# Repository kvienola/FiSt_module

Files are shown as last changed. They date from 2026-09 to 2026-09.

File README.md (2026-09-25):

# Fixation-Stimulus (FiSt) module for mirror-based adaptive optics scanning systems

This repository contains all the files related to the FiSt module to recreate it for your own use. The main goal of the module is to work as a stand-alone unit to be incorporated to existing imaging systems and allow precise stimulus delivery for optoretinographic measurements. The folders contain STL files that can be directly 3D printed, STP files that allow you to modify components according to your needs and Zemax files to simulate the fixation and stimulus path separately when altering components.

If you find the module and its files useful in your research, we kindly ask you to cite our publication XXX. 

__Maciej M. Bartuzel, PhD__ \
maciej.bartuzel@pwr.edu.pl

Department of Biomedical Engineering  
Wroclaw University of Science and Technology

## 1. 3D-printing
There are no restrictions what type of printing method you use or what type of filament. The Gen 1 module was printed using black PLA filament. We also recommend using high enough infill to ensure the rigidity of the different parts. And if you are not familiar with using thread inserts, we recommend printing a test block and practice. It is not difficult, but better to ruin a small sample block than ready-make larger component.

## 2. CAD design
Besides just the STL files, the folders contain also STP files that are meant for the community to develop further. If you make new version of certain components or add something useful, feel free to send us the files and we are more than happy to then include them in this repository.

## 3. Zemax simulations
The current two files (.zmx) simulate the fixation path and stimulus path separately using the currently selected components.

## 4. Future improvements planned for the module

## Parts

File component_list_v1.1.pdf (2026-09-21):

Component | Manufacturer | Model number | Quantity | Price per unit | Total cost | Description | Link
Aspherized Achromatic Lens | Edmund Optics | #49-656 | 1 | $113.95 | $113.95 | 9mm Diameter x 12mm EFL Aspherized Achromatic Lens | https://www.edmundoptics.com/p/9mm-diameter-x-12mm-efl-aspherized-achromatic-lens/10162/
Filter Holder | Edmund Optics | #54-996 | 1 | $67.50 | $67.50 | 15mm Sq., Fixed Filter Holder | https://www.edmundoptics.com/p/15mm-sq-fixed-filter-holder/11731/
75 x 75 mm Flat mirror | Edmund Optics | #88-541 | 2 | $301.00 | $602.00 | 75 x 75mm Protected Silver, λ/4 Mirror | https://www.edmundoptics.com/p/75-x-75mm-protected-silver-lambda4-mirror/30799/
Ø1" Achromatic Doublet | Thorlabs | AC254-075-A | 1 | $95.34 | $95.34 | f = 75 mm, Ø1" Achromatic Doublet, ARC: 400 - 700 nm | https://www.thorlabs.com/item/AC254-075-A
Ø2" Achromatic Doublet | Thorlabs | AC508-150-A | 2 | $132.19 | $264.38 | f = 150 mm, Ø2" Achromatic Doublet, ARC: 400 - 700 nm | https://www.thorlabs.com/item/AC508-150-A
Mounting Fork | Thorlabs | BP207 | 1 | $55.62 | $55.62 | Mounting Fork for Ø2" Pellicle Beamsplitters | https://www.thorlabs.com/item/BP207
Ø2" Pellicle Beamsplitter | Thorlabs | BP208 | 1 | $152.54 | $152.54 | Ø2" Pellicle Beamsplitter, Uncoated for 8:92 (R:T) Split Ratio for 400-2400 nm | https://www.thorlabs.com/item/BP208
XY adjustment plate | Thorlabs | CP1XY | 1 | $474.12 | $474.12 | 30 mm Cage XY Flexure Adjustment Plate | https://www.thorlabs.com/item/CP1XY
Iris Diaphragm | Thorlabs | CP20D | 1 | $111.60 | $111.60 | 30 mm Cage System Iris Diaphragm (Ø0.8 - Ø20 mm) | https://www.thorlabs.com/item/CP20D
Cage rod | Thorlabs | ER3 | 4 | $7.64 | $30.56 | Cage Assembly Rod, 3" Long, Ø6 mm | https://www.thorlabs.com/item/ER3
Kinematic mirror mount | Thorlabs | KMSS/M | 3 | $43.61 | $130.83 | Compact Kinematic Mirror Mount, Hex Adjuster, M4 Taps for Post Mounting | https://www.thorlabs.com/item/KMSS_M
Ø1" Bi-Convex Lens | Thorlabs | LB1294-A | 1 | $40.36 | $40.36 | N-BK7 Bi-Convex Lens, Ø1", f = 175.0 mm, ARC: 350 - 700 nm | https://www.thorlabs.com/item/LB1294-A
Fiber Patch Cable | Thorlabs | M45L01 | 1 | $95.21 | $95.21 | Ø400 µm, 0.50 NA, SMA-SMA Fiber Patch Cable, Low OH, 1 m Long | https://www.thorlabs.com/item/M45L01
2" x 2" Mirror | Thorlabs | PFSQ20-03-P01 | 1 | $144.90 | $144.90 | 2" x 2" Protected Silver Mirror | https://www.thorlabs.com/item/PFSQ20-03-P01
Retaining Ring | Thorlabs | SM1RR | 1 | $5.21 | $5.21 | SM1 Retaining Ring for Ø1" Lens Tubes and Mounts | https://www.thorlabs.com/item/SM1RR
Z-axis translation mount | Thorlabs | SM1ZB/M | 1 | $235.61 | $235.61 | Z-Axis Translation Mount, 30 mm Cage Compatible, M4 x 0.7 Tap | https://www.thorlabs.com/item/SM1ZB_M
Fiber adapter plate | Thorlabs | SM05SMA | 1 | $35.59 | $35.59 | SMA Fiber Adapter Plate with External SM05 (0.535"-40) Threads | https://www.thorlabs.com/item/SM05SMA
Fiber-coubled LED | Thorlabs | MINTF4 | 1 | $623.08 | $623.08 | 554 nm, 21 mW (Min) Fiber-Coupled LED, 1225 mA, SMA | https://www.thorlabs.com/item/MINTF4
LED Driver | Thorlabs | LEDD1B | 1 | $380.04 | $380.04 | T-Cube LED Driver, 1200 mA Max Drive Current (Power Supply Not Included) | https://www.thorlabs.com/item/LEDD1B
Power Supply for LED Driver | Thorlabs | KPS201 | 1 | $43.15 | $43.15 | 15 V, 2.66 A Power Supply Unit with 3.5 mm Jack Connector for One K- or T-Cube | https://www.thorlabs.com/item/KPS201
Threaded insert kit for 3D prints | FFVRVSS | 600Pcs M2-M6 Kit+Tools | 1 | $14.99 | $14.99 | 600+7Pcs Brass Threaded Inserts M2 M2.5 M3 M4 M5 M6 for 3D Printing | https://www.amazon.com/FFVRVSS-M2-M3-Threaded-Inserts/dp/B0FWCHPY4F/ref=sr_1_3
6mm Bore Dia Linear Motion Bushings | Various | not specific | 1 | $9.99 | $9.99 | Linear Bearings, 6mm Bore Dia Linear Motion Bushing with Double Side Rubber Seal | https://www.amazon.com/MELIFE-Bearings-Bushing-Machine-Printer/dp/B0CL3WD28D/ref=sr_1_4
M8 threaded rod, L = 200 mm | Various | not specific | 1 | $7.19 | $7.19 | 304 Stainless Steel M8-1.25 Fully All Threaded Rod, 250 mm length | https://www.amazon.com/Feelers-Stainless-M8-1-25-Threaded-Length%E3%80%90Pack/dp/B08FQL7LXV
6 mm unthreaded rod, L = 200 mm | Various | not specific | 2 | $6.17 | $12.34 | 304 Stainless Steel 6 x 200mm Round Rods | https://www.amazon.com/Eowpower-Stainless-Steel-200mm-Turning/dp/B072JPQX4Q
PLA filament | SUNLU | | 1 | $13.99 | $13.99 | PLA 3D Printer Filament, Black, 1KG | https://www.amazon.com/Printer-Filament-SUNLU-Dimensional-Accuracy/dp/B07XG3RM58
LCD screen + Driver board | Sharp | LS029B3SX01 | 1 | $94.81 | $94.81 | 2.9 Inch LCD Display LS029B3SX01 + driver | https://www.aliexpress.com/item/1005005565755501.html
Large dichroic mirror | CHROMA | T715LP | 1 | - | - | Dichroic BS with 715 nm cut-off, currently not in production. Alternative option: | https://www.idex-hs.com/store/product-detail/ff700_di01_25x36
A ball bearing | Various | not specific | 1 | $6.79 | $6.79 | A ball bearing with 8 mm ID and 12 mm OD. Maximum thickness of 12.7 mm. | https://www.amazon.com/MR128-2RS-Groove-Bearings-Robotics-Electric/dp/B0DXV273BX/ref=sr_1_1
| | | | | $3,854.90
| | | | | $2,808.63

Threaded inserts, rods, bearings do not need to be any specific manufacturer, as long as they are within specifications listed. Links are given as examples.

### Total cost

Excl. LED and driver

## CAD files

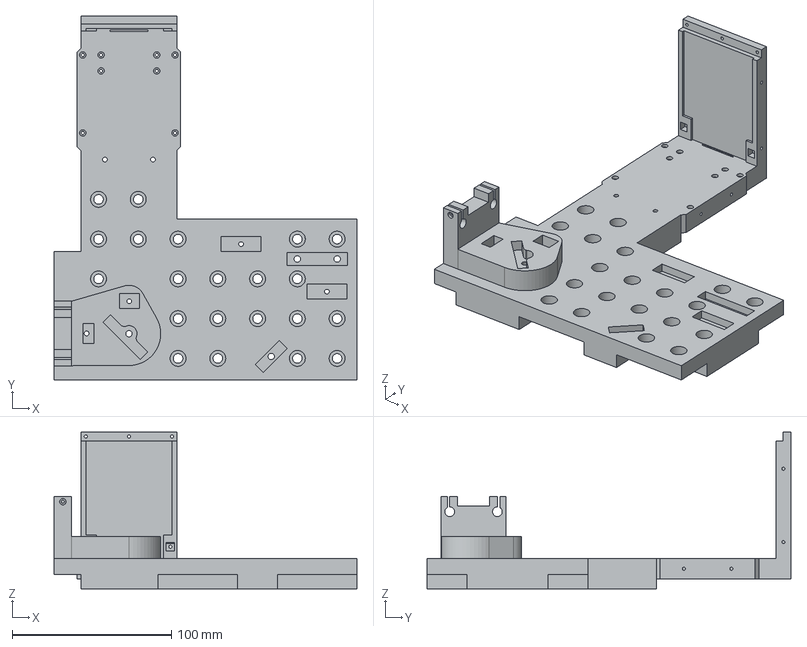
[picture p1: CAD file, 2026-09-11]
Main board/stp/01_mainboard.stp
190.5 x 228.8 x 98.7 mm

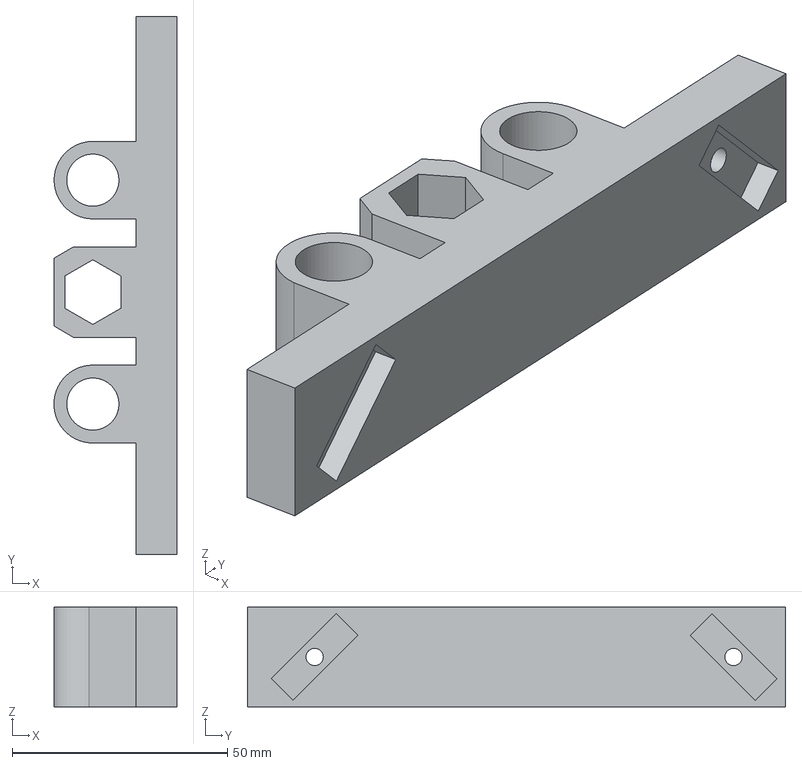
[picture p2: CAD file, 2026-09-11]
Badal stage/stp/13_badal_stage_top.stp
28.5 x 124.9 x 23.1 mm

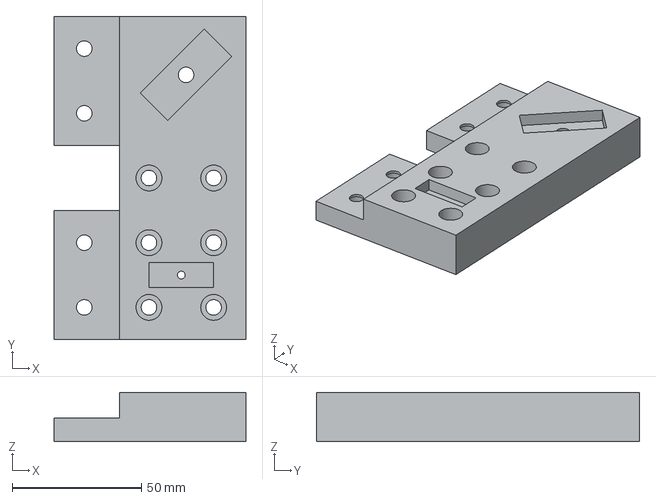
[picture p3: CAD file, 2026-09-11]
Imaging board/stp/23_dichroic_board.stp
74.2 x 125.0 x 19.1 mm

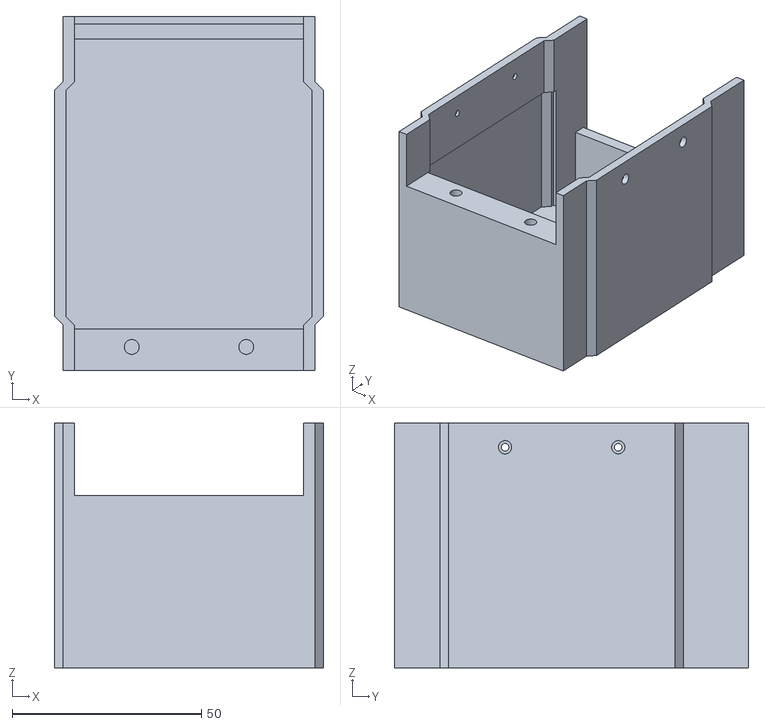
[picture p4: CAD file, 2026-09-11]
Main board/stl/04_pcb_boards_housing.stl
71.0 x 93.5 x 64.6

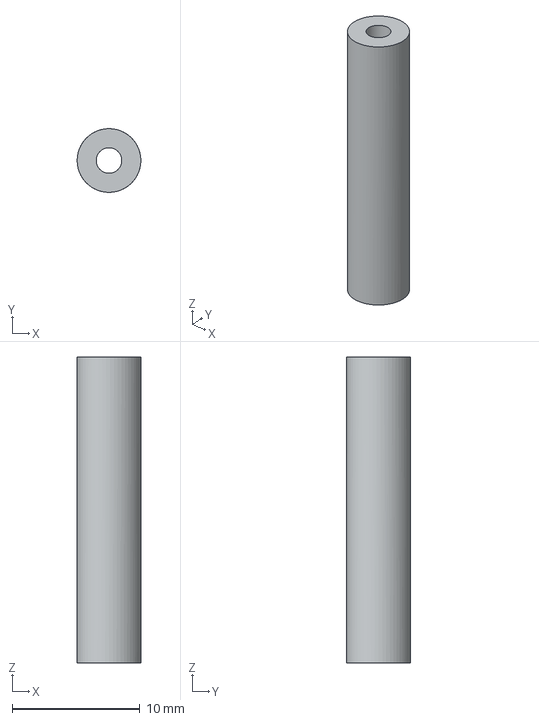
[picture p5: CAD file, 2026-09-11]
Main board/stp/02_electronics_post_24mm.stp
5.00 x 5.00 x 24.0 mm

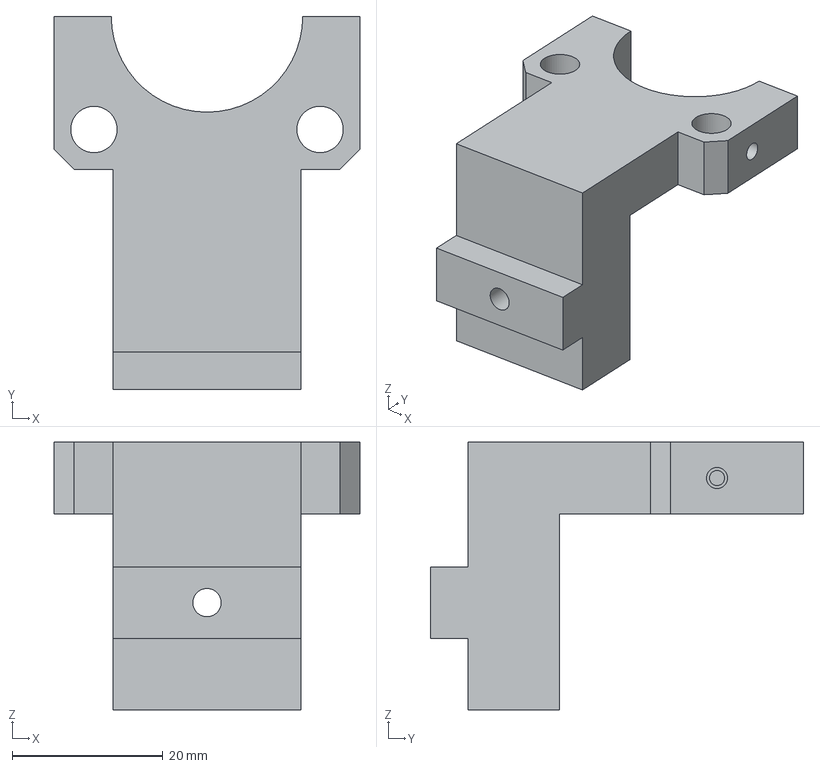
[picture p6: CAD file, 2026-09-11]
Stimulus board/stp/27_cage_system_insert_iris_holder.stp
40.6 x 49.5 x 35.5 mm

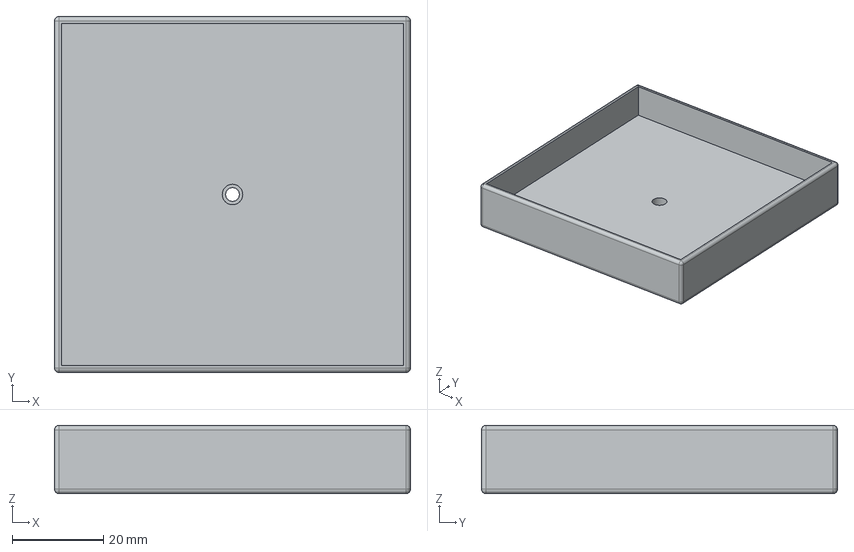
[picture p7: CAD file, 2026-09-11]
Badal stage/stp/15_square_mirror_holder_large.stp
78.0 x 78.0 x 15.0 mm

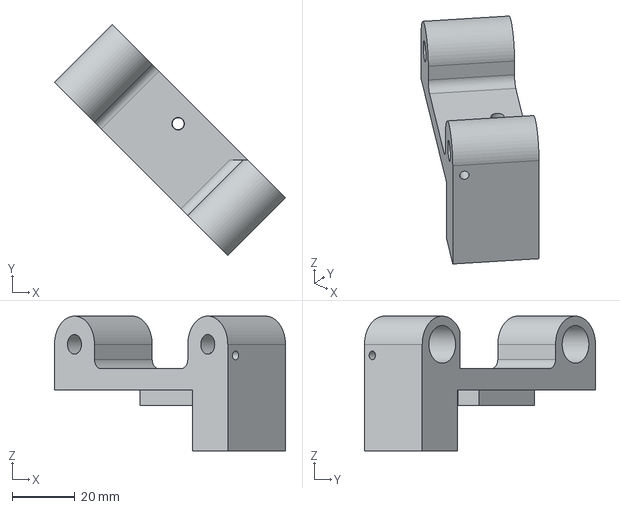
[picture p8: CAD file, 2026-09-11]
Imaging board/stp/25_rods_guiding_addon.stp
73.5 x 73.5 x 42.9 mm

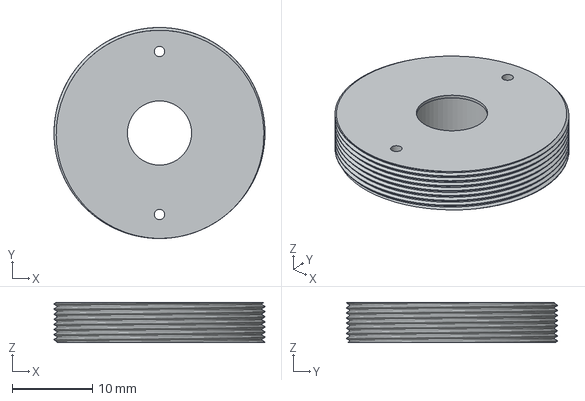
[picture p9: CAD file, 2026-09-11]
Stimulus board/stp/29_collimator_lens_holder_tube.stp
26.3 x 26.3 x 5.00 mm

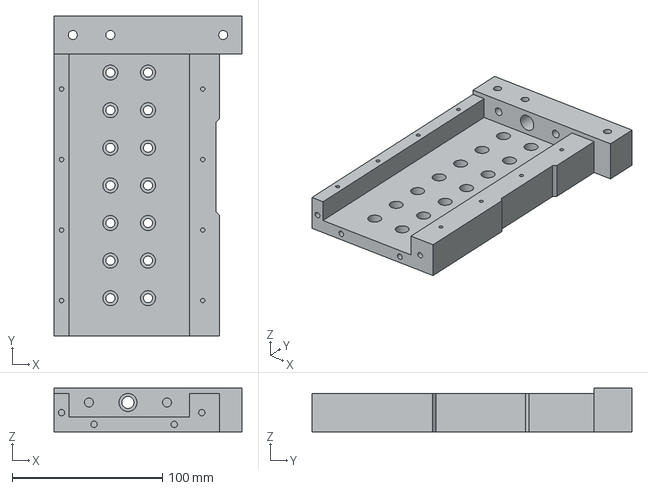
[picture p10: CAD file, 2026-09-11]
Badal stage/stp/12_badal_stage_bottom.stp
125.0 x 212.5 x 29.1 mm

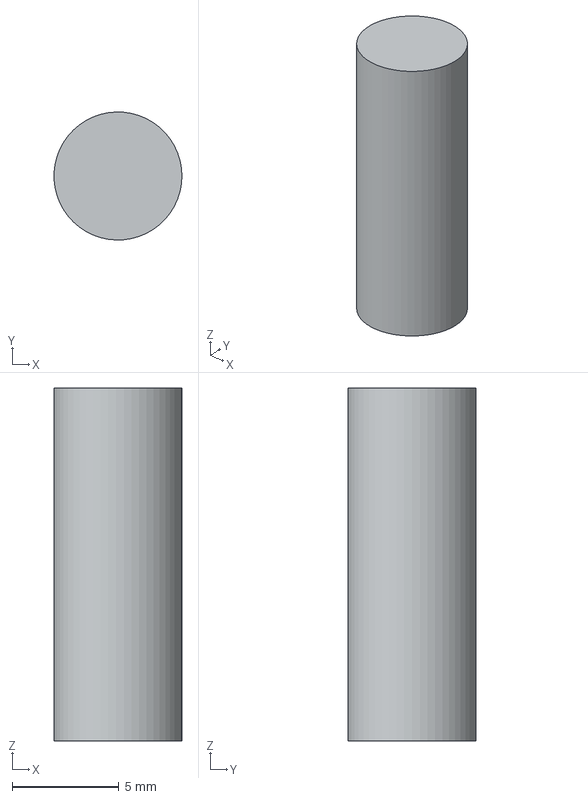
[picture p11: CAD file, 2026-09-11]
Main board/stp/11_iris_mounting_rod.stp
5.99 x 6.00 x 16.5 mm

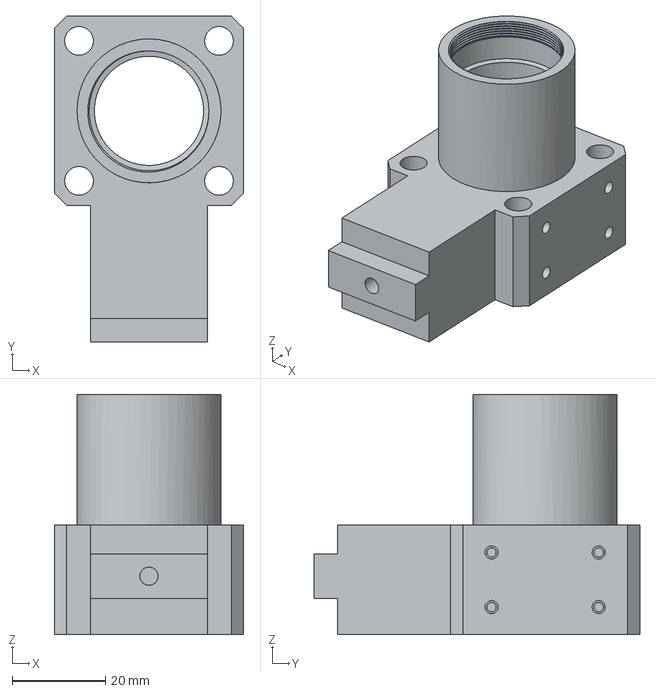
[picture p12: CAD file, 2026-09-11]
Stimulus board/stp/28_stimulus_cage_system_insert.stp
40.6 x 69.8 x 51.4 mm

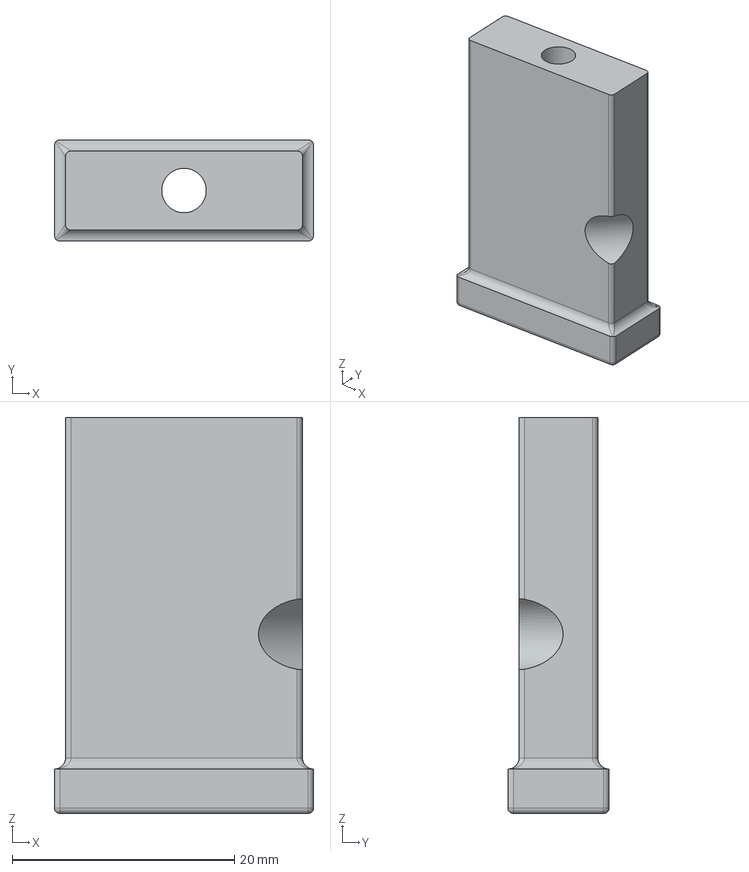
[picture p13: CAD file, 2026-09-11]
Main board/stp/08_square_mirror_support_with_6mm_rod_cutout.stp
23.3 x 9.11 x 35.6 mm

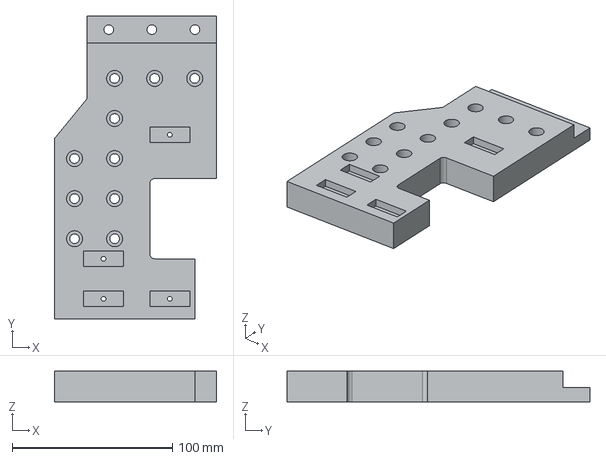
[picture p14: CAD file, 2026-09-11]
Stimulus board/stp/26_stimulus_board.stp
101.1 x 188.9 x 19.1 mm

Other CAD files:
Main board/stp/04_pcb_board_housing.stp
Imaging board/stp/24_dichroic_holder.stp
Main board/stp/07_square_mirror_holder_small.stp
Main board/stp/05_lcd_screen_front_panel.stp
Badal stage/stl/12_badal_stage_bottom.stl
Badal stage/stl/13_badal_stage_top.stl
Badal stage/stl/14_square_mirror_support_badal_stage.stl
Badal stage/stl/15_square_mirror_holder_large.stl
Badal stage/stl/16_square_mirror_holder_large_cut_corner.stl
Badal stage/stl/17_badal_screw_8mm_end_cap.stl
Badal stage/stl/18_badal_screw_8mm_front_cap.stl
Badal stage/stl/19_badal_screw_8mm_rotating_handle.stl
Badal stage/stl/20_badal_screw_handle_fixing_bolt.stl
Badal stage/stl/21_badal_stage_cover_rear.stl
Badal stage/stl/22_badal_stage_cover_top.stl
Badal stage/stp/14_square_mirror_support_Badal_stage.stp
Badal stage/stp/16_square_mirror_holder_large_cut_corner.stp
Badal stage/stp/17_badal_screw_8mm_end_cap.stp
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

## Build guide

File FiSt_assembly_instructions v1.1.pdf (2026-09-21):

# Fixation-Stimulus channel (FiSt)

# Assembly instructions

v1.1

# Main board

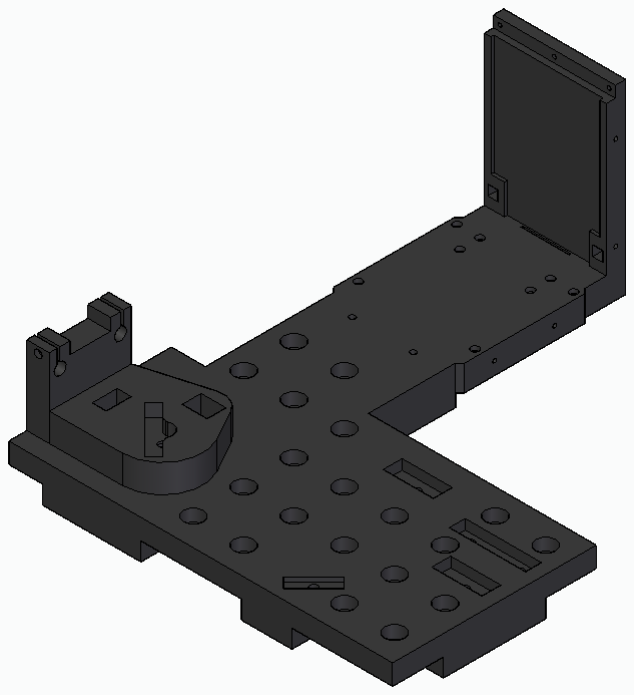
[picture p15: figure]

## Needs to be 3D-printed: 1 × 01_mainboard 4 × 02_electronics_post_24mm 4 × 03_electronics_post_10mm

## Installing PCB mounting brackets

# Main board

## Installing PCB mounting brackets

Use 8 × M2 socket head
screws to fix the posts to the main board.

Main board | (a)

## Installing PCB boards

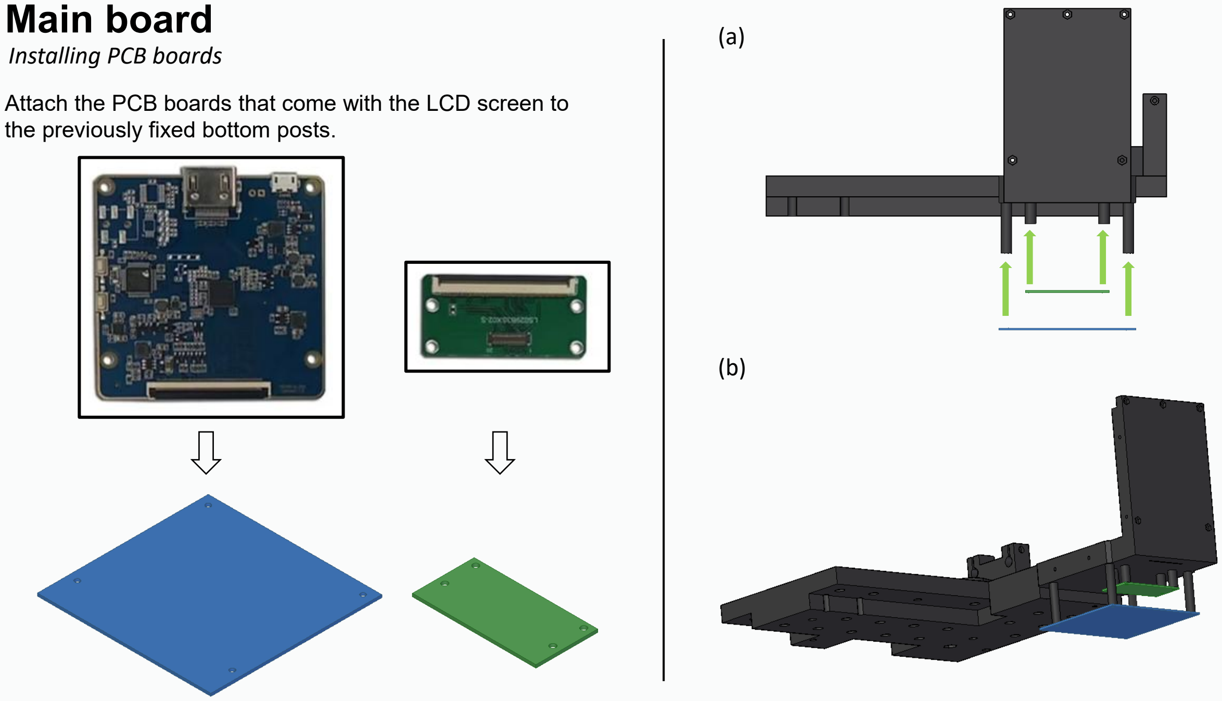
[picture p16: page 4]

Attach the PCB boards that come with the LCD screen to the previously fixed bottom posts.

(b)

# Main board

## PCB enclosure

Mold the M3 threaded inserts into the designated holes (red arrows) on both sides using a soldering tool.

## Needs to be 3D-printed: 1 × 04_PCB_boards_housing

# Main board

## PCB enclosure

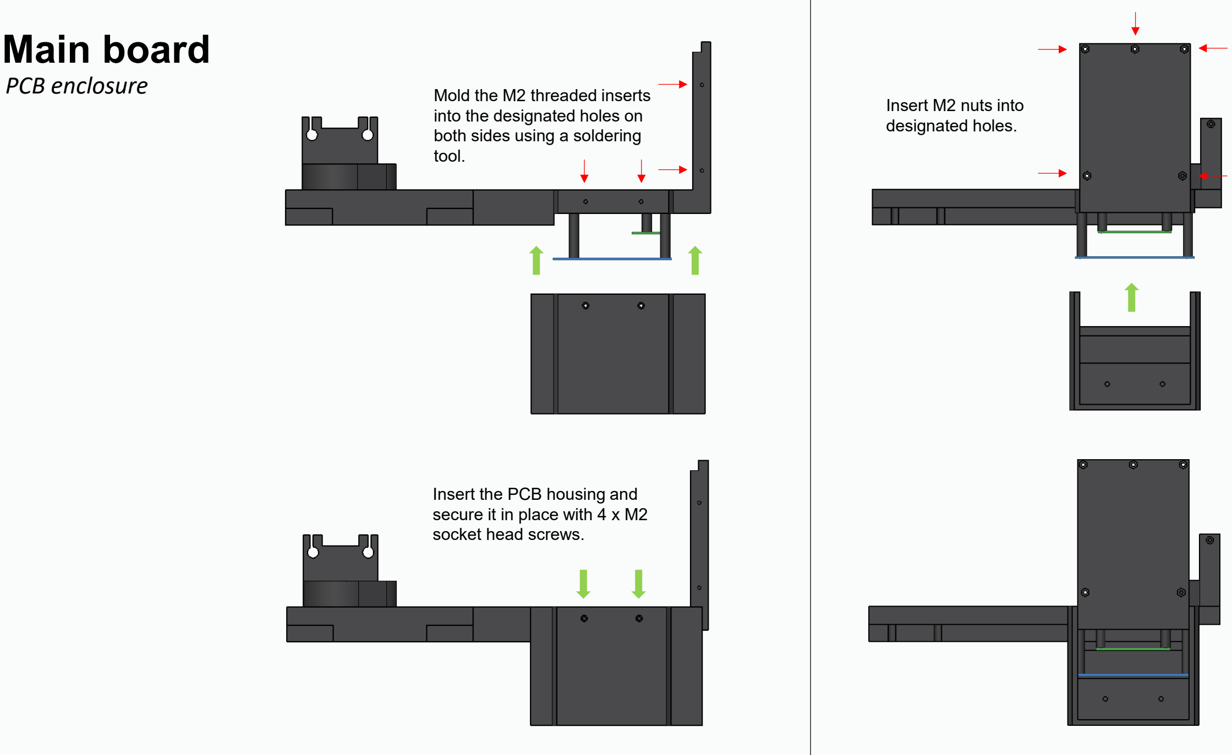
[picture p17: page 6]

Mold the M2 threaded inserts into the designated holes on both sides using a soldering tool.

Insert M2 nuts into
designated holes.

Insert the PCB housing and secure it in place with 4 x M2 socket head screws.

# Main board

## Inserting LCD screen

Insert the screen into
designated slot.

Pass the flat flex cable
(not visualized in the
magnified image) through
the designated slot as
indicated by green
arrows.

Connect the cable to the
green PCB board

LCD screen

# Main board

## Inserting LCD screen

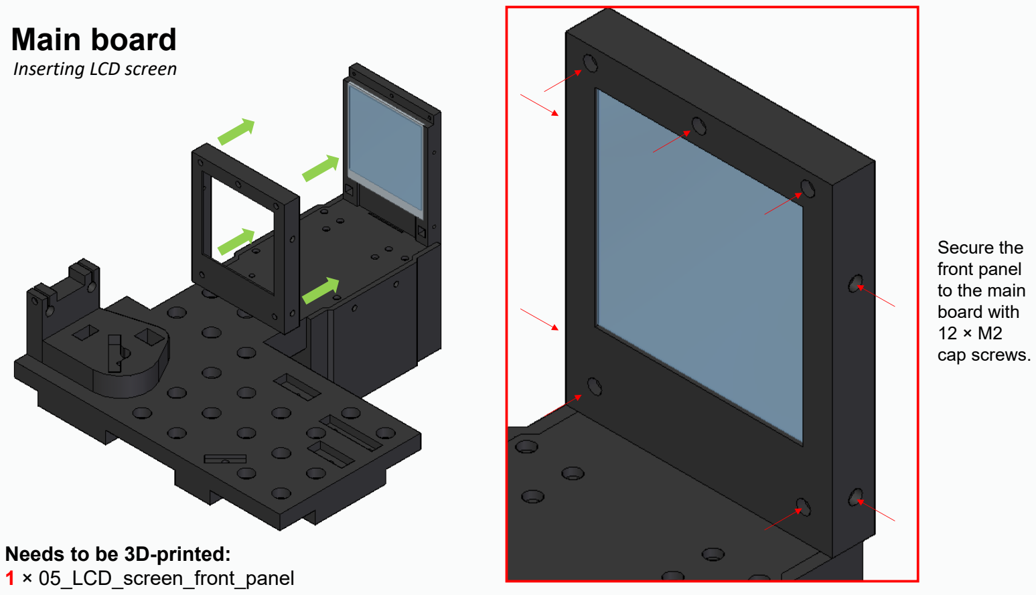
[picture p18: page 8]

Secure the
front panel
to the main
board with
12 × M2
cap screws.

## Needs to be 3D-printed: 1 × 05_LCD_screen_front_panel

# Main board

(a) (b)

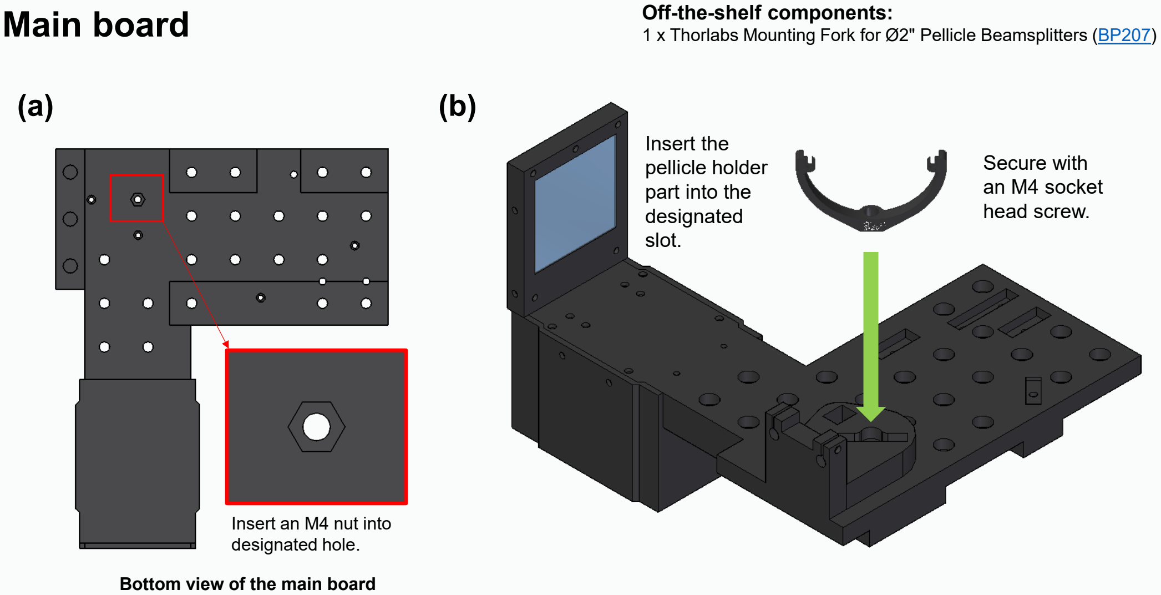
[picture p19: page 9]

Insert an M4 nut into
designated hole.

Bottom view of the main board

Insert the
pellicle holder
part into the
designated
slot.

Secure with
an M4 socket
head screw.

Off-the-shelf components:
1 x Thorlabs Mounting Fork for Ø2" Pellicle Beamsplitters (BP207) (https://www.thorlabs.com/item/BP207)

Main board | Off-the-shelf components:

## Needs to be 3D-printed: 2 × 06_two_inch_lens_clamp_holder 1 × 2in_lens_clamp_holder_mounting_tool (optional)

Mold M3 threaded inserts into the designated holes indicated by the red arrows.

Insert M3 nuts into the designated slots indicated by the green arrows.

2 x Achromatic Doublet (AC508 (https://www.thorlabs.com/item/AC508-150-A)- (https://www.thorlabs.com/item/AC508-150-A)150 (https://www.thorlabs.com/item/AC508-150-A)- (https://www.thorlabs.com/item/AC508-150-A)A) (https://www.thorlabs.com/item/AC508-150-A)

# Main board

Once in the proper
position, secure the lens
using an M3 cap screw.

# Main board

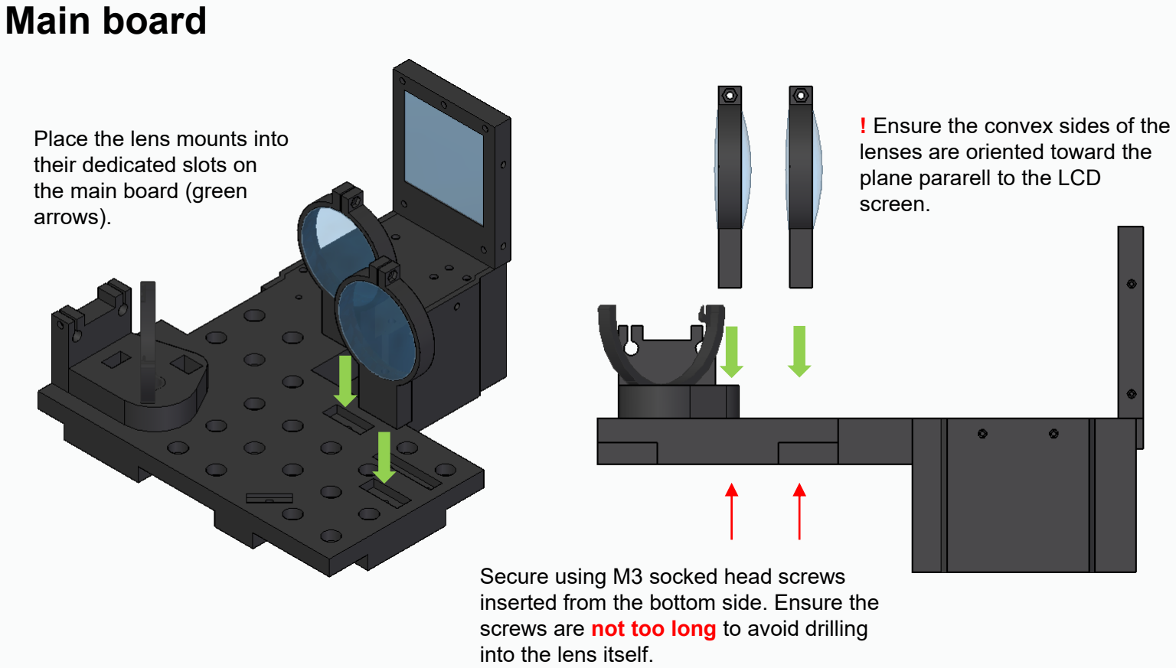
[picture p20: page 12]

Secure using M3 socked head screws inserted from the bottom side. Ensure the screws are not too long to avoid drilling into the lens itself.

! Ensure the convex sides of the lenses are oriented toward the plane pararell to the LCD
screen.

Place the lens mounts into their dedicated slots on
the main board (green
arrows).

Main board | Off-the-shelf components needed 1 × Thorlabs 2" x 2" Protected Silver Mirror (PFSQ20 (https://www.thorlabs.com/item/PFSQ20-03-P01)- (https://www.thorlabs.com/item/PFSQ20-03-P01)03 (https://www.thorlabs.com/item/PFSQ20-03-P01)- (https://www.thorlabs.com/item/PFSQ20-03-P01)P01) (https://www.thorlabs.com/item/PFSQ20-03-P01)

## Needs to be 3D-printed: 1 × 07_square_mirror_holder_small 1 × 08_square_mirror_support_with_6mm_rod_cutout

1 × Thorlabs Compact Kinematic Mirror Mount (KMSS (https://www.thorlabs.com/item/KMSS_M)/ (https://www.thorlabs.com/item/KMSS_M)M) (https://www.thorlabs.com/item/KMSS_M)

2.

# Main board

Secure using 4-40 socket
head screw.

Ensure the
corresponding
surfaces are as
parallel as possible. 1.

Ensure the position of the cutout is as indicated.

Slide the kinematic mount
into the post holder as tight as possible. Be careful as it may fall off – final fixing is with the M4 cap screw in
the next step.

3.

Insert the mirror
into the holder
with a tight fit.

Fit the support post into the slot indicated by the green arrow. Secure the assembly using an M4 socket head screw, as indicated by the red arrow. The screw should be long enough to go through the main board and the post holder and reach the threading of the kinematic mount.

4.

## Off-the-shelf components needed 1 × Pellicle Beamsplitter (BP208) (https://www.thorlabs.com/item/BP208)

Mold M3 threaded
inserts into the
designated holes
indicated by the red
arrows.

Insert M2 nuts into
the designated
slots indicated by
the green arrows.

1 × Ø1" Achromatic Doublet (AC254 (https://www.thorlabs.com/item/AC254-075-A)- (https://www.thorlabs.com/item/AC254-075-A)075 (https://www.thorlabs.com/item/AC254-075-A)- (https://www.thorlabs.com/item/AC254-075-A)A) (https://www.thorlabs.com/item/AC254-075-A)

## 1 x Iris diapraghm (CP20D) (https://www.thorlabs.com/item/CP20D)

1 x Ø1" Bi-Convex Lens (LB1294 (https://www.thorlabs.com/item/LB1294-A)- (https://www.thorlabs.com/item/LB1294-A)A) (https://www.thorlabs.com/item/LB1294-A)

# Main board

## Needs to be 3D-printed: 1 × 09_one_inch_lens_clamp_holder_stim 1 × 10_one_inch_lens_clamp_holder_fix 2 x 11_iris_mounting_rod

# Main board

## Installing pellicle BS

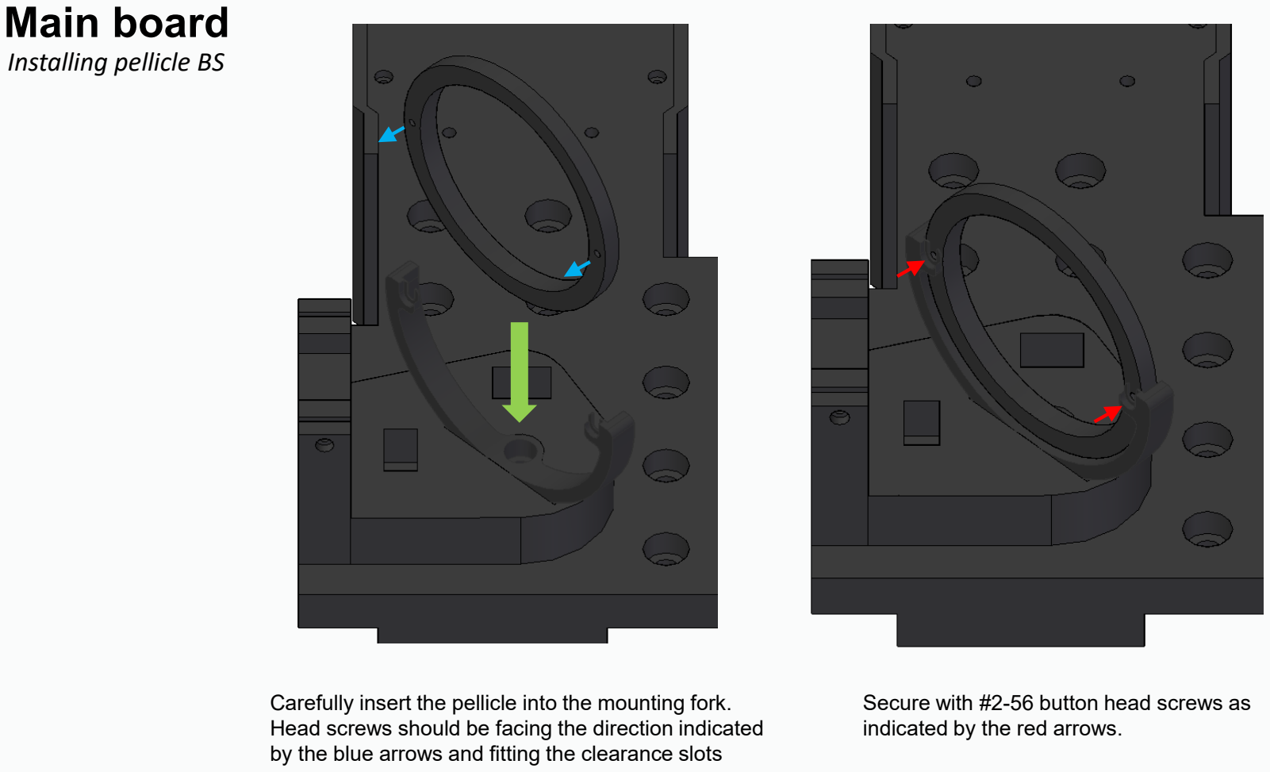
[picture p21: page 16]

Secure with #2-56 button head screws as indicated by the red arrows.

Carefully insert the pellicle into the mounting fork. Head screws should be facing the direction indicated by the blue arrows and fitting the clearance slots

1.

2. 3.

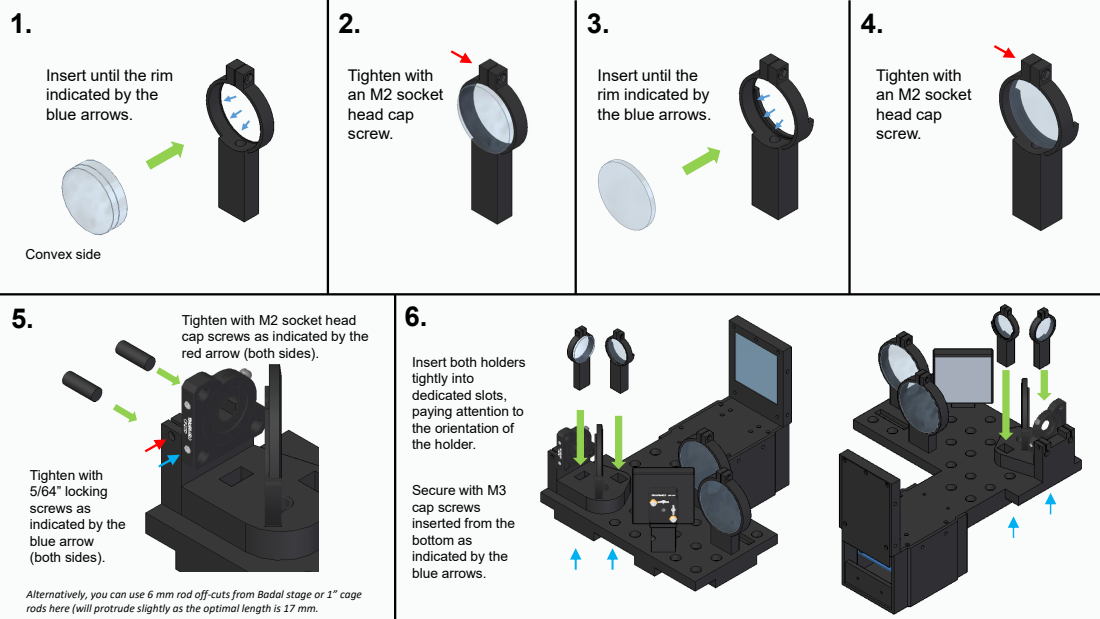
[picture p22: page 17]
Tighten with an M2 socket head cap screw.; Convex side

Insert until the rim
indicated by the
blue arrows.

Insert until the
rim indicated by
the blue arrows.

Tighten with M2 socket head
cap screws as indicated by the
red arrow (both sides).

Insert both holders
tightly into
dedicated slots,
paying attention to
the orientation of
the holder.

Tighten with
5/64” locking
screws as
blue arrow
(both sides).

Secure with M3
cap screws
inserted from the
bottom as

Alternatively, you can use 6 mm rod off-cuts from Badal stage or 1” cage
rods here (will protrude slightly as the optimal length is 17 mm.

# Main board

## Complete!

Badal stage | Off-the-shelf components needed 2 × sliding rod (Ø6mm, L = 200 mm)

Mold the M3 threaded inserts into the designated holes (green arrows) using a soldering tool.

Mold the M6 threaded inserts into the designated holes (blue arrows) using a soldering tool.

Mold the M2 threaded inserts into the designated holes (red arrows) on both sides using a soldering tool.

## Needs to be 3D-printed: 1 × 12_badal_stage_bottom

# Badal stage

## Translation stage base

Slide the rods into the
designated slots for a tight fit.

Ensure the end tips of the rods are flush with the encasing.

## Off-the-shelf components needed 2 × Kinematic mirror mount (KMSS/M) (https://www.thorlabs.com/item/KMSS_M)

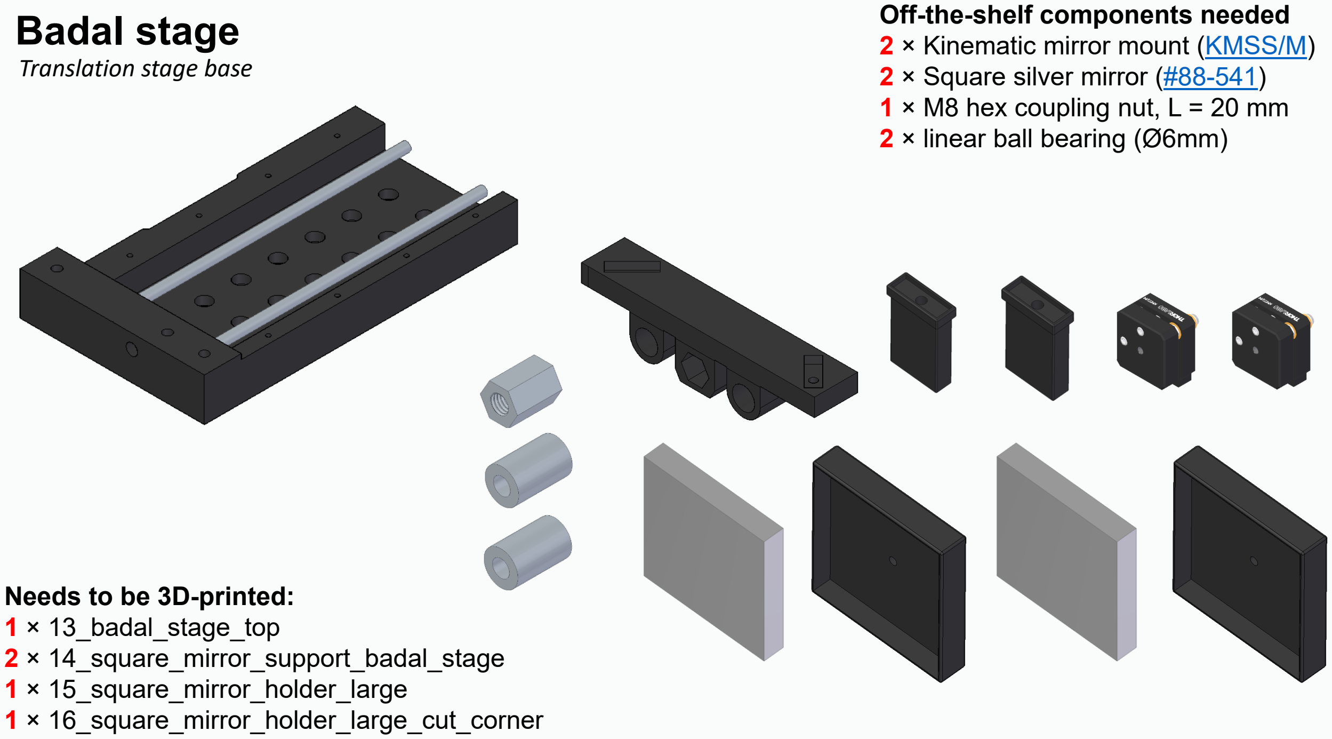
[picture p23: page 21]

## Needs to be 3D-printed: 1 × 13_badal_stage_top 2 × 14_square_mirror_support_badal_stage 1 × 15_square_mirror_holder_large 1 × 16_square_mirror_holder_large_cut_corner

2 × Square silver mirror (#88 (https://www.edmundoptics.com/p/75-x-75mm-protected-silver-lambda4-mirror/30799/)- (https://www.edmundoptics.com/p/75-x-75mm-protected-silver-lambda4-mirror/30799/)541) (https://www.edmundoptics.com/p/75-x-75mm-protected-silver-lambda4-mirror/30799/)

## 1 × M8 hex coupling nut, L = 20 mm 2 × linear ball bearing (Ø6mm)

# Badal stage

## Translation stage base

1.

Badal stage | 4.

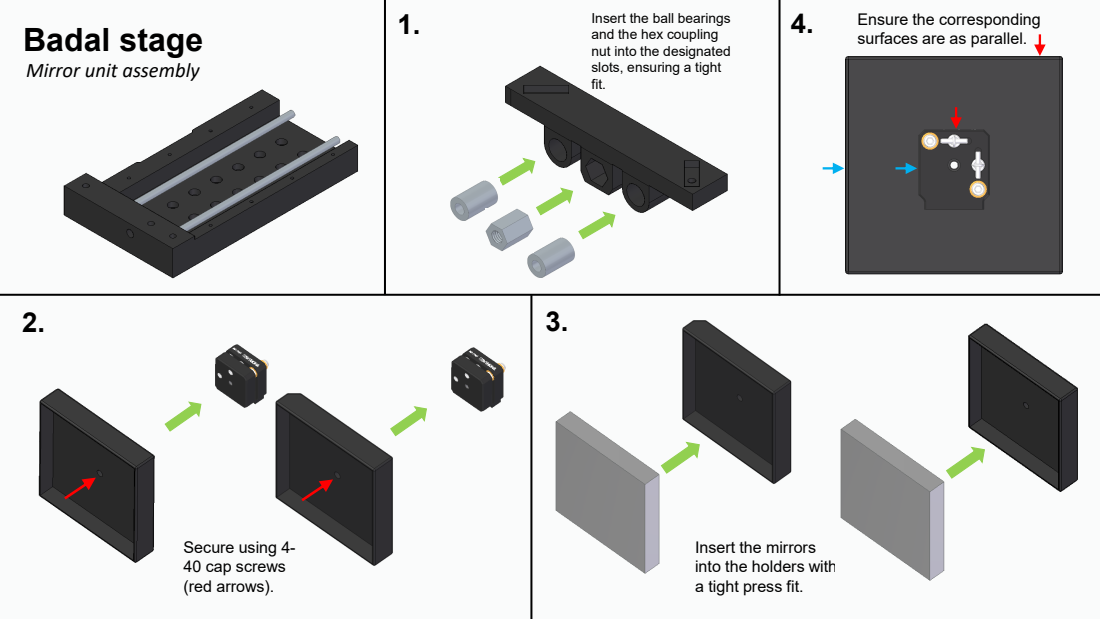
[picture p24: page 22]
Secure using 4- 40 cap screws (red arrows).

Insert the ball bearings
and the hex coupling
nut into the designated
slots, ensuring a tight
fit.

Ensure the corresponding
surfaces are as parallel.

Mirror unit assembly

Insert the mirrors
into the holders with
a tight press fit.

1

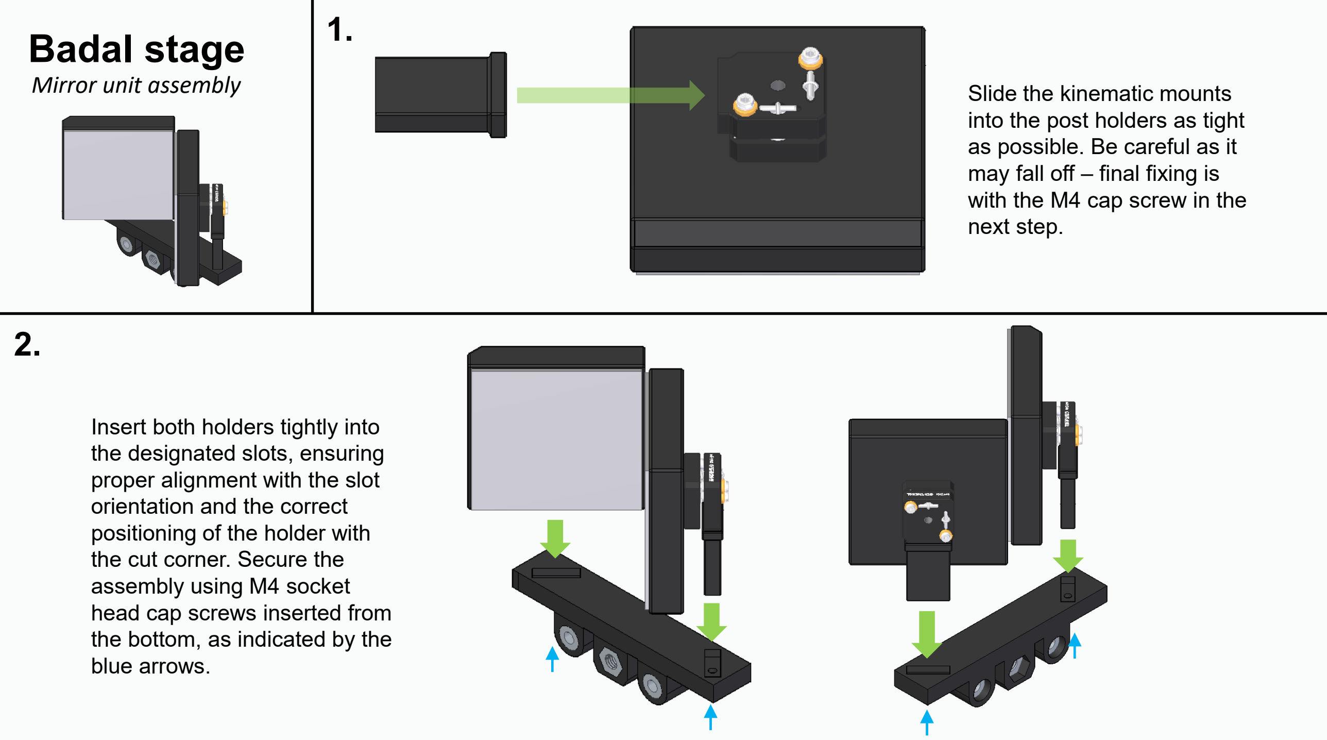
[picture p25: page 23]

Slide the kinematic mount

s
into the post holder

s as tight
as possible. Be careful as it may fall off

– final fixing is
with the M4 cap screw in the next step

Insert both holders tightly into the designated slots, ensuring proper alignment with the slot orientation and the correct positioning of the holder with the cut corner. Secure the assembly using M4 socket
head cap screws inserted from the bottom, as indicated by the blue arrows.

2.

# Badal stage

## Mirror unit assembly

Off-the-shelf components needed Badal stage | 1 × M8 threaded rod, L = 215 mm

## Movement assembly

## Needs to be 3D-printed: 1 × 17_Badal_screw_8mm_end_cap 1 × 18_Badal_screw_8mm_front_cap 1 × 19_Badal_screw_8mm_rotating_handle 2 × 20_Badal_screw_handle_fixing_bolt 1 × 21_Badal_stage_cover_rear 1 × 22_Badal_stage_cover_top

1. 2.

Align with the top stage cover.

Insert the threaded rod into the central assembly through the designated slot with hex coupling (blue arrow in inset). Attach end and front caps by rotating as indicated by the blue arrows until the fit is tight.

Slide the handle part of the rod (the one with the two holes) into the slot on the rear stage holder. Ensure it fits snugly and aligns with the holder.

Attach the rotating handle and secure with the two fixing bolts.

3. 4.

## Off

## -the

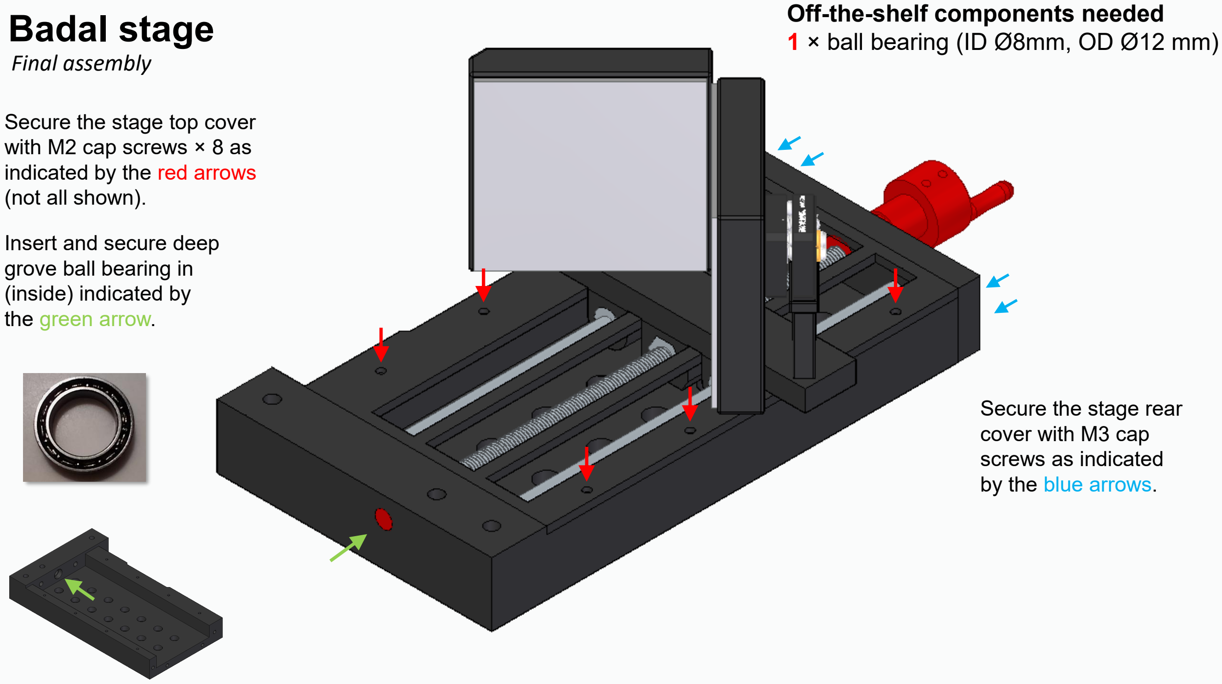
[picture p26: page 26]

Insert and secure deep
grove ball bearing in
(inside) indicated by
the green arrow.

Secure the stage top cover with M2 cap screws

× 8 as
indicated by the red arrows (not all shown)

Secure the stage rear
cover with M3 cap
screws as indicated
by the blue arrows

-shelf components needed Badal stage | 1 × ball bearing (ID Ø8mm, OD Ø12 mm)

## Final assembly

# Badal stage

## Complete!

# Connecting Badal stage

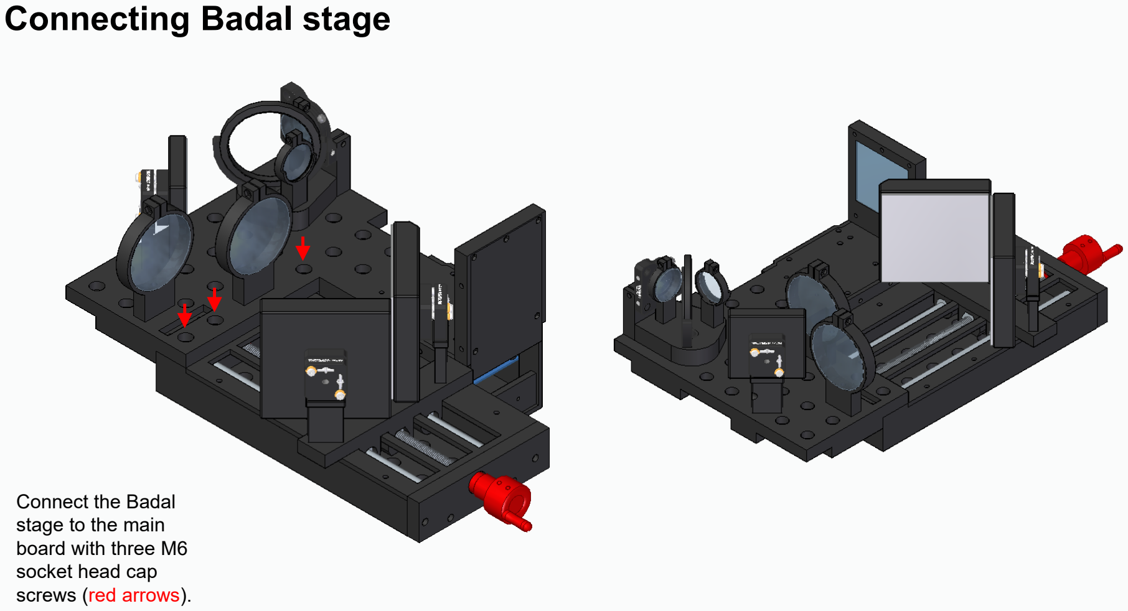
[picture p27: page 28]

Connect the Badal
stage to the main
board with three M6
socket head cap
screws (red arrows).

## Attach element 23 to the Main board assembly first. Then proceed as the

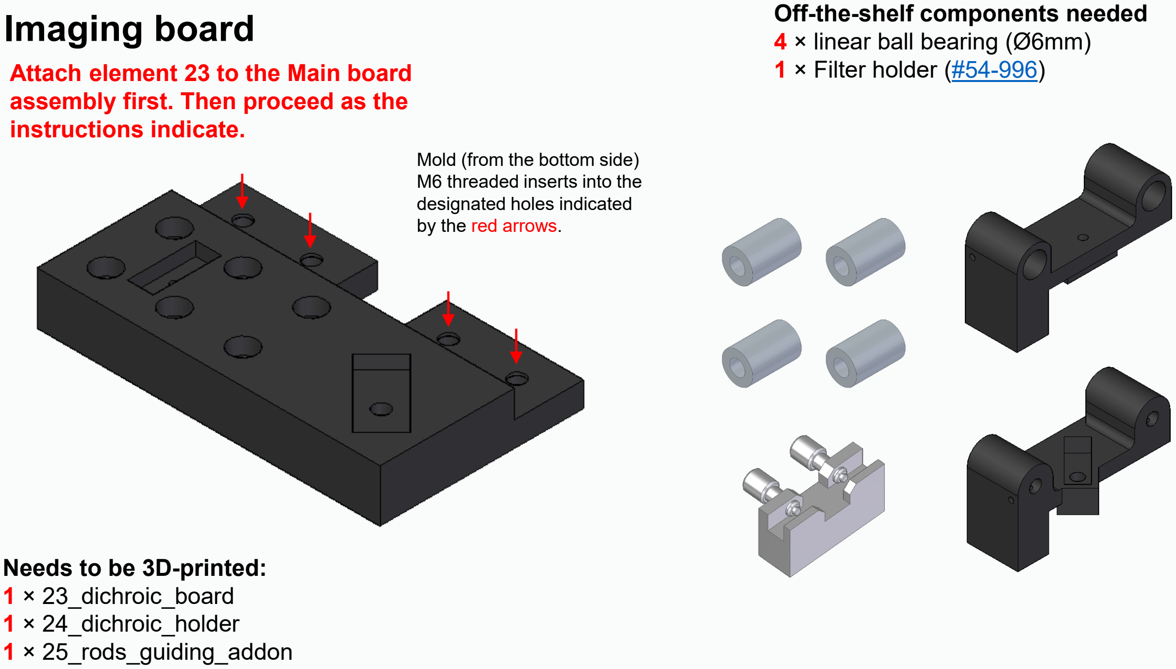
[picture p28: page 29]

## Needs to be 3D-printed: 1 × 23_dichroic_board 1 × 24_dichroic_holder 1 × 25_rods_guiding_addon

instructions indicate.

Mold (from the bottom side) M6 threaded inserts into the designated holes indicated by the red arrows.

## Off-the-shelf components needed 4 × linear ball bearing (Ø6mm)

1 × Filter holder (#54 (https://www.edmundoptics.com/p/15mm-sq-fixed-filter-holder/11731/)- (https://www.edmundoptics.com/p/15mm-sq-fixed-filter-holder/11731/)996) (https://www.edmundoptics.com/p/15mm-sq-fixed-filter-holder/11731/)

# Imaging board

1. | 2. | 3.

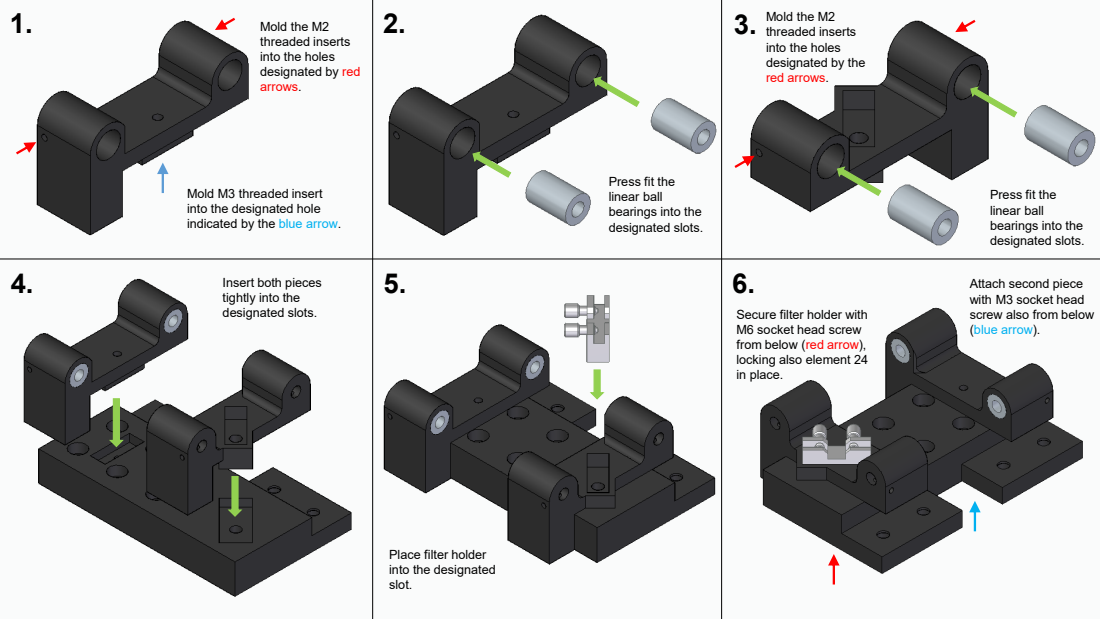
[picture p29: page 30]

Mold the M2
threaded inserts
into the holes
designated by the
red arrows.

designated by red
arrows.

Press fit the
linear ball
bearings into the
designated slots.

Mold M3 threaded insert
into the designated hole
indicated by the blue arrow.

4. Insert both pieces

6. Attach second piece

tightly into the

with M3 socket head
screw also from below
(blue arrow).

Secure filter holder with
M6 socket head screw
from below (red arrow),
locking also element 24
in place.

Place filter holder
into the designated
slot.

# Imaging board added

## Note: Here you can see why the element 23

## was connected to the main board first as the two other pieces go on top of the main

board.

## Before proceeding to building the stimulus board, mold M6

threaded inserts into the holes designated by the red arrows.

# Imaging board added

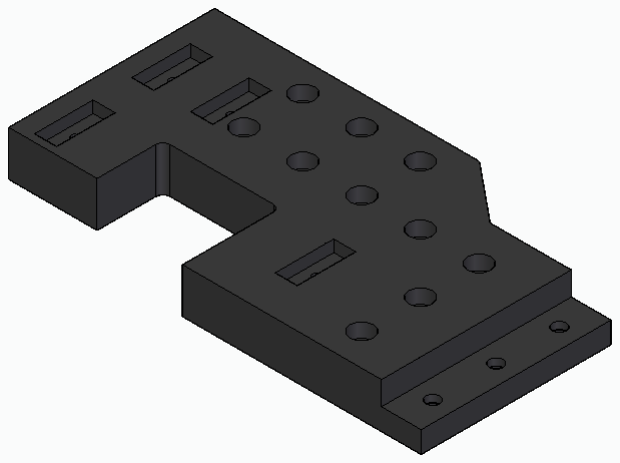
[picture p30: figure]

## Needs to be 3D-printed: 1 × 26_stimulus_board 1 × 28_stimulus_cage_system_insert 1 × 27_cage_system_insert_iris_holder 2 × 11_iris_mounting_rod

Stimulus board | Off-the-shelf components needed 1 × Ø1” achromatic doublet (AC254 (https://www.thorlabs.com/thorproduct.cfm?partnumber=AC254-075-A)- (https://www.thorlabs.com/thorproduct.cfm?partnumber=AC254-075-A)075 (https://www.thorlabs.com/thorproduct.cfm?partnumber=AC254-075-A)- (https://www.thorlabs.com/thorproduct.cfm?partnumber=AC254-075-A)A) (https://www.thorlabs.com/thorproduct.cfm?partnumber=AC254-075-A) 1 × retainer ring (SM1RR) (https://www.thorlabs.com/thorproduct.cfm?partnumber=SM1RR) 1 × Iris Diaphragm (CP20D) (https://www.thorlabs.com/thorproduct.cfm?partnumber=CP20D)

1

. | 2. | 3.

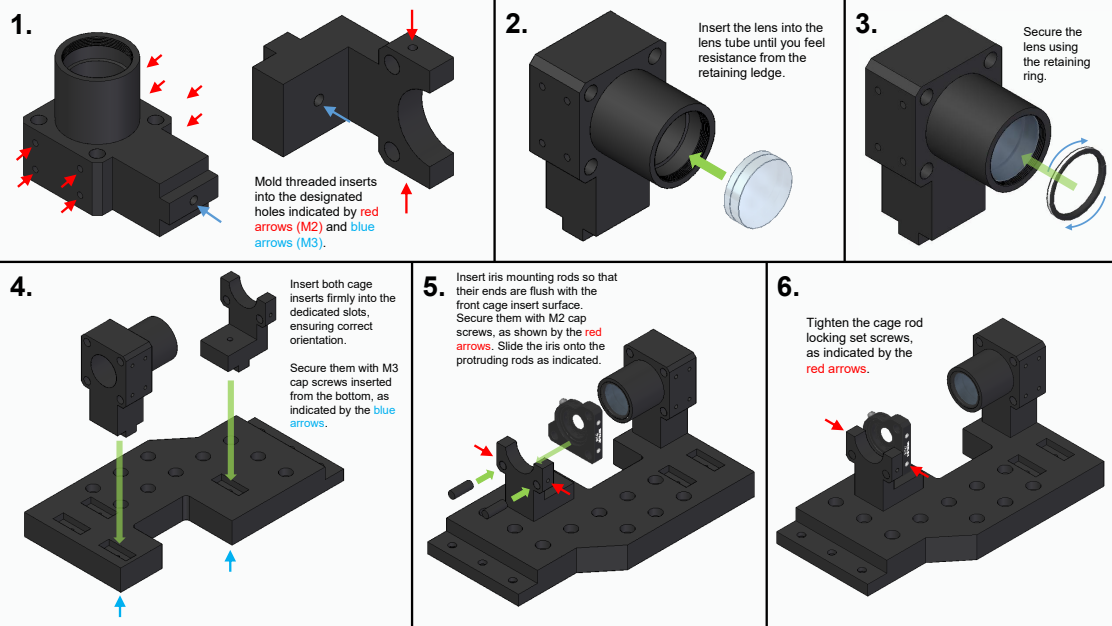
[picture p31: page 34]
Secure the lens using the retaining ring.

Insert the lens into the
lens tube until you feel
resistance from the
retaining ledge.

Mold threaded inserts
into the designated
holes indicated by red
arrows (M2) and blue
arrows (M3)

Insert iris mounting rods so that
their ends are flush with the
front cage insert surface.
Secure them with M2 cap
screws, as shown by the red
arrows. Slide the iris onto the
protruding rods as indicated.

Insert both cage
inserts firmly into the
dedicated slots,
ensuring correct
orientation.

Tighten the cage rod
locking set screws,
as indicated by the
red arrows

Secure them with M3
cap screws inserted
from the bottom, as
indicated by the blue
arrows

## Off-the-shelf components needed 4 × Cage rod 3 inch (ER3) (https://www.thorlabs.com/item/ER3)

## Needs to be 3D-printed: 1 × 29_collimator_lens_holder_tube

1 × Aspherized Achromat (#49 (https://www.meetoptics.com/lenses/achromatic/aspherized-achromat/s/edmund-optics/p/49-656)- (https://www.meetoptics.com/lenses/achromatic/aspherized-achromat/s/edmund-optics/p/49-656)656) (https://www.meetoptics.com/lenses/achromatic/aspherized-achromat/s/edmund-optics/p/49-656)

## 1 × Cage XY adjustment plate (CP1XY) (https://www.thorlabs.com/item/CP1XY#ad-image-0) 1 × SMA Fiber Adapter Plate (SM05SMA) (https://www.thorlabs.com/item/SM05SMA#ad-image-0) 1 × Z-Axis Translation Mount (SM1ZA) (https://www.thorlabs.com/item/SM1ZA)

# Stimulus board

1. | 2. | 3.

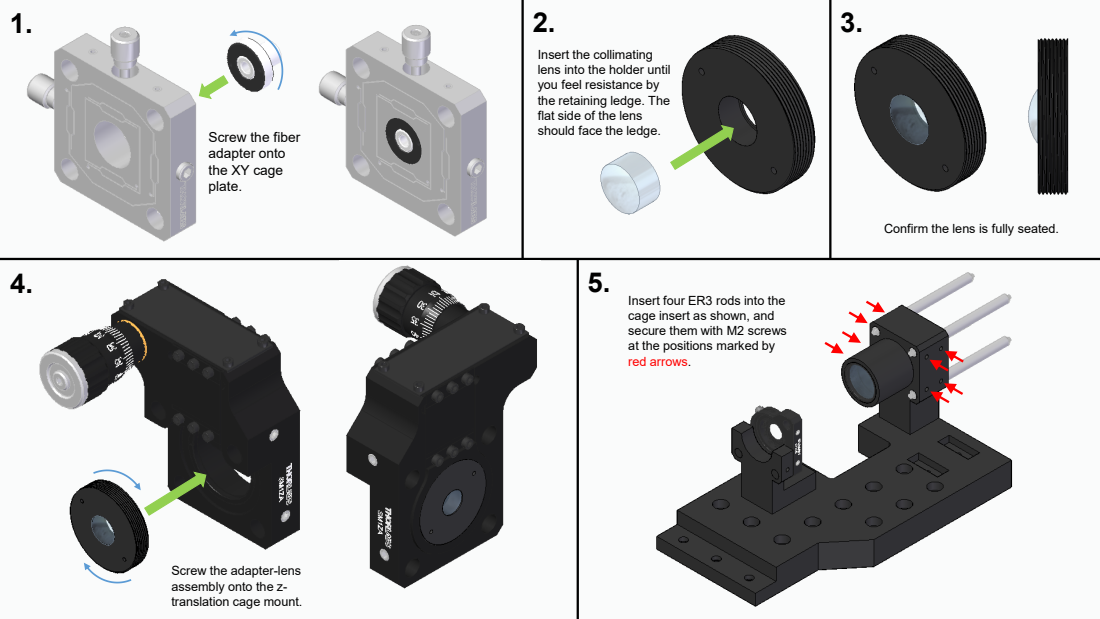
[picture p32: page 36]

Insert the collimating
lens into the holder until
you feel resistance by
the retaining ledge. The
flat side of the lens
should face the ledge.

Screw the fiber
adapter onto
the XY cage
plate.

Confirm the lens is fully seated.

Insert four ER3 rods into the
cage insert as shown, and
secure them with M2 screws
at the positions marked by
red arrows.

Screw the adapter-lens
assembly onto the z-
translation cage mount.

1

. | 2.

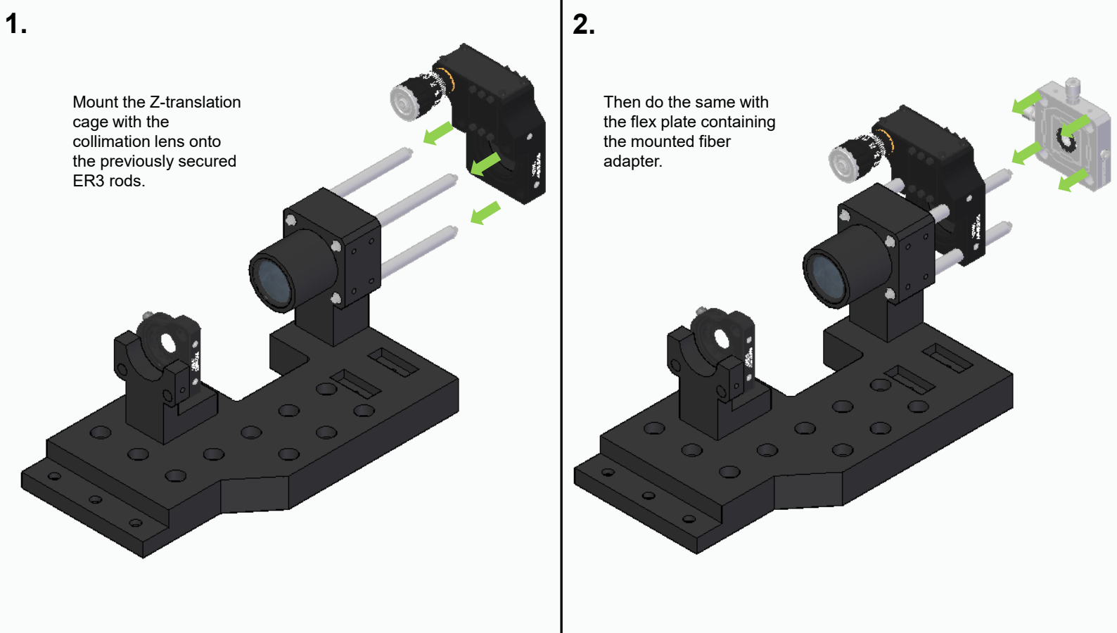
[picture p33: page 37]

Mount the Z

-translation
cage with the
collimation lens onto
the previously secured
ER3 rods.

Then do the same with
the flex plate containing
the mounted fiber
adapter.

# Stimulus board

# Connecting stimulus board to the main assembly

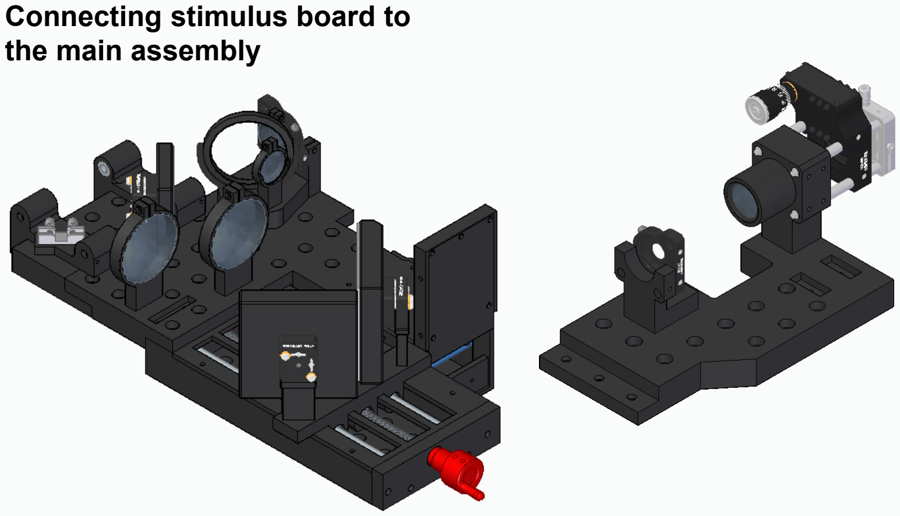
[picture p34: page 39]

# Connecting stimulus board to the main assembly

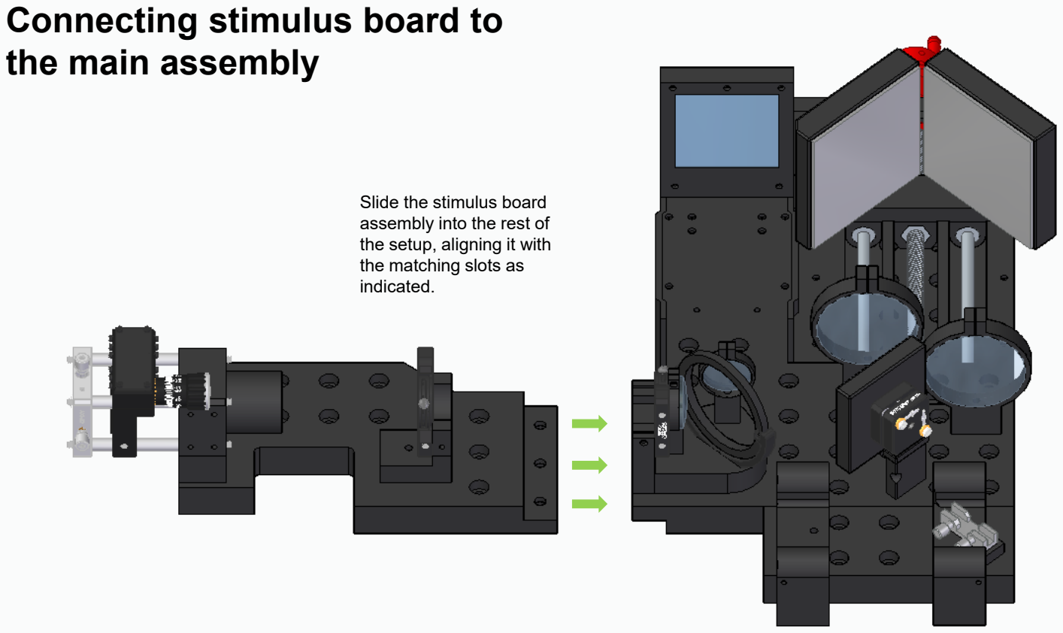
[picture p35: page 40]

Slide the stimulus board
assembly into the rest of
the setup, aligning it with the matching slots as
indicated.

# Connecting stimulus board to the main assembly

Tightly secure with M6 cap screws as indicated with the red arrows to the previously molded thread inserts.

# FiSt module complete

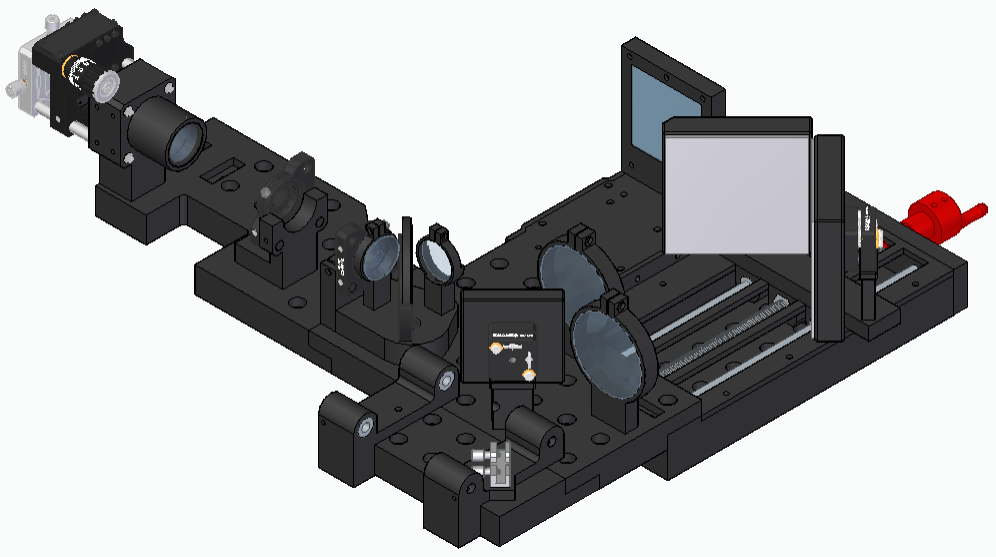
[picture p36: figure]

# Installing posts

## Needs to be 3D-printed: 3 × 30_mounting_post_long 1 × 31_mounting_post_short

## Mold M6 threaded inserts into each hole at the top of each post (insert

from the top side).

Note! The length of the posts can be altered to match the beam height of your optical system.

# Installing posts

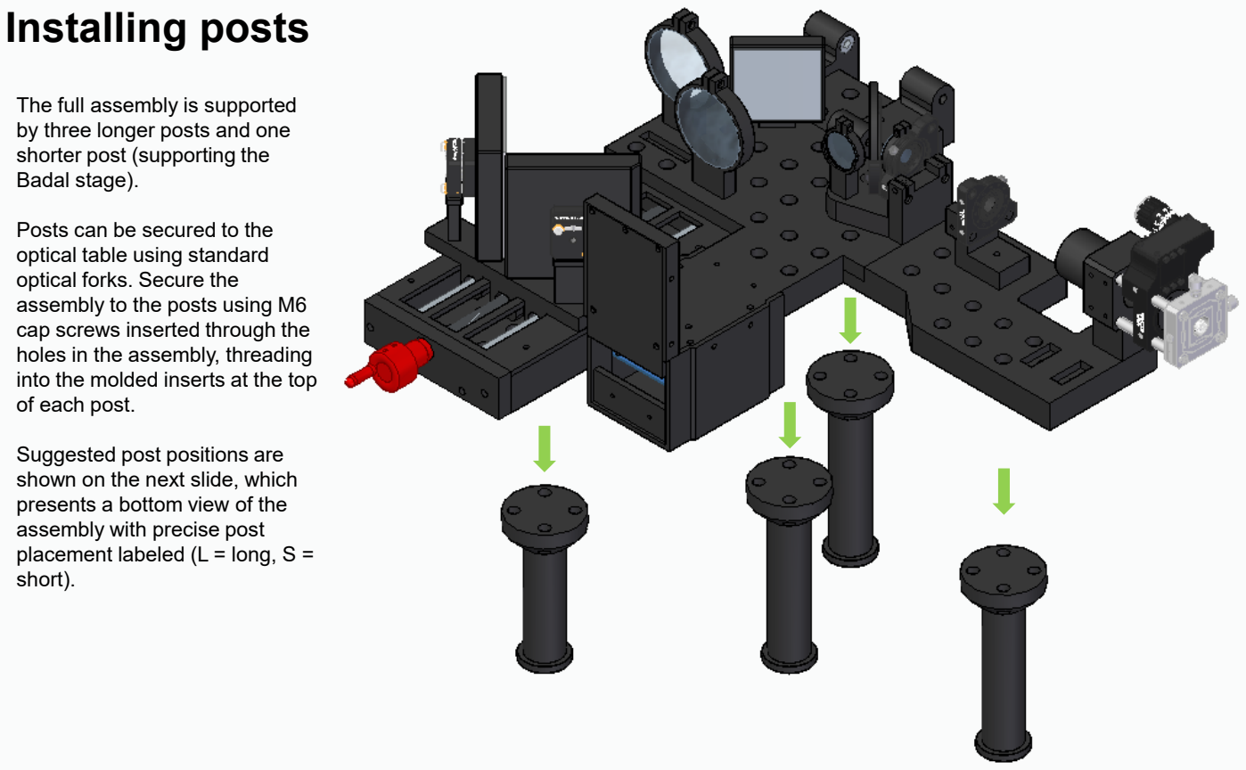
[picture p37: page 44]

The full assembly is supported by three longer posts and one shorter post (supporting the Badal stage).

Posts can be secured to the optical table using standard optical forks. Secure the
assembly to the posts using M6 cap screws inserted through the holes in the assembly, threading into the molded inserts at the top of each post.

Suggested post positions are shown on the next slide, which presents a bottom view of the assembly with precise post placement labeled (L = long, S = short).

# Installing posts

L
L

L

S

## L = long post S = short post

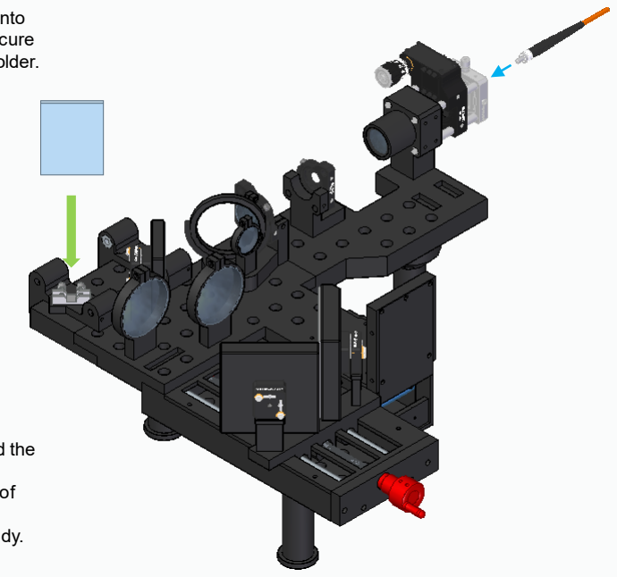
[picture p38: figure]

Insert the dichroic mirror into designated holder and secure using the screws in the holder.

Insert the multimode fiber tip into the entry of the stimulus channel (blue arrow). Tighten the screw to the fiber adapter.

After inserting the fiber and the dichroic mirror you may
proceed to final alignment of the optics. The stimulus-fixation channel is now ready.
Final notes | Off-the-shelf components 1 × Multimode fiber (M45L01) (https://www.thorlabs.com/thorproduct.cfm?partnumber=M45L01) 1 × Dichroic mirror (TP715lp)

# Final notes
